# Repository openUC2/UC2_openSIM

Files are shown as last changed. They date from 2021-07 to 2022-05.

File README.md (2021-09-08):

<p align="left">

</p>

# openUC2 openSIM
---

This is the repository for the openSIM project which integrates structured illumination microscopy into the UC2-system.

🧾 The manuscript for the openISM and openSIM can be found under the [DOI:10.1101/2021.01.08.425840](https://doi.org/10.1101/2021.01.08.425840)

<p align="center">
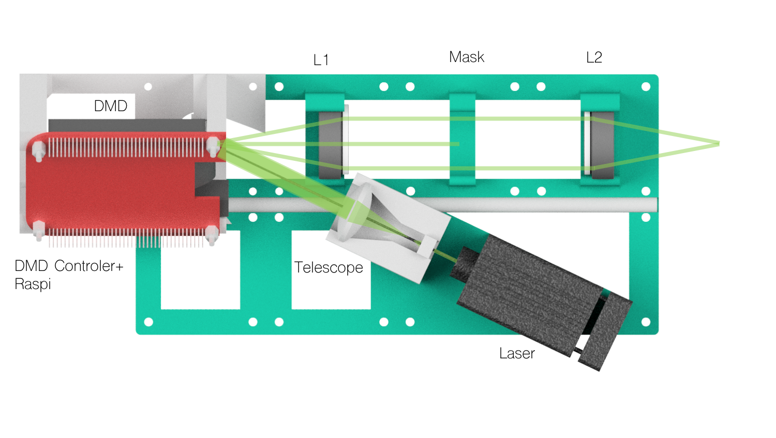
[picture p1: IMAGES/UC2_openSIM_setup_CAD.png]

</p>

***Fig 1:*** *This is the ready-to-print module which clicks into the UC2-system*

This module is based on the work by the Huser-Lab and can be found as a preprint on Bioarxiv [1]. It uses a low-cost single-mode diode laser (532 nm) and a Raspberry Pi driven DMD module to generate a structured illumination for microscopy. Since we use coherent illumination, we can create pattern suitable for SIM in order to increase the lateral resolution. So far we're not aiming for any super-resolution, but rather give a proof of principle.  

<p align="center">
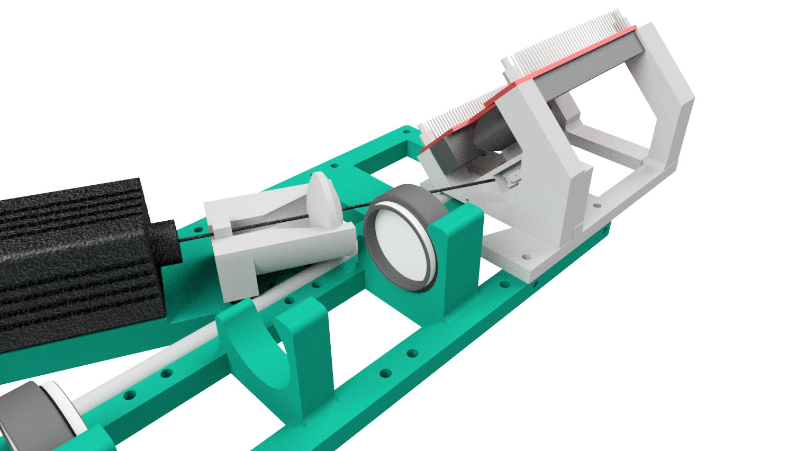
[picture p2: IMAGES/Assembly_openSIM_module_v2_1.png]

</p>

***Fig 2:*** *A beam-expander magnifies the collimated beam which hits the DMD displaying a set of gratings*

The angle between the collimated and expanded Laser-beam and the DMD is 25° in order to get the maximum in the diffracted orders.

[1] *DMD-based super-resolution structured illumination microscopy visualizes live cell dynamics at high speed and low cost
Alice Sandmeyer, Mario Lachetta, Hauke Sandmeyer, Wolfgang Hübner, Thomas Huser, Marcel Müller
bioRxiv 797670; doi: [https://doi.org/10.1101/797670](https://doi.org/10.1101/797670)*

***Features:***
- "True" two-beam SIM
- Very low cost:  ~400€
- Easy to align
- Open-Source
- One module per wavelength possible
- Various patterns possible

## Optical System

<p align="center">
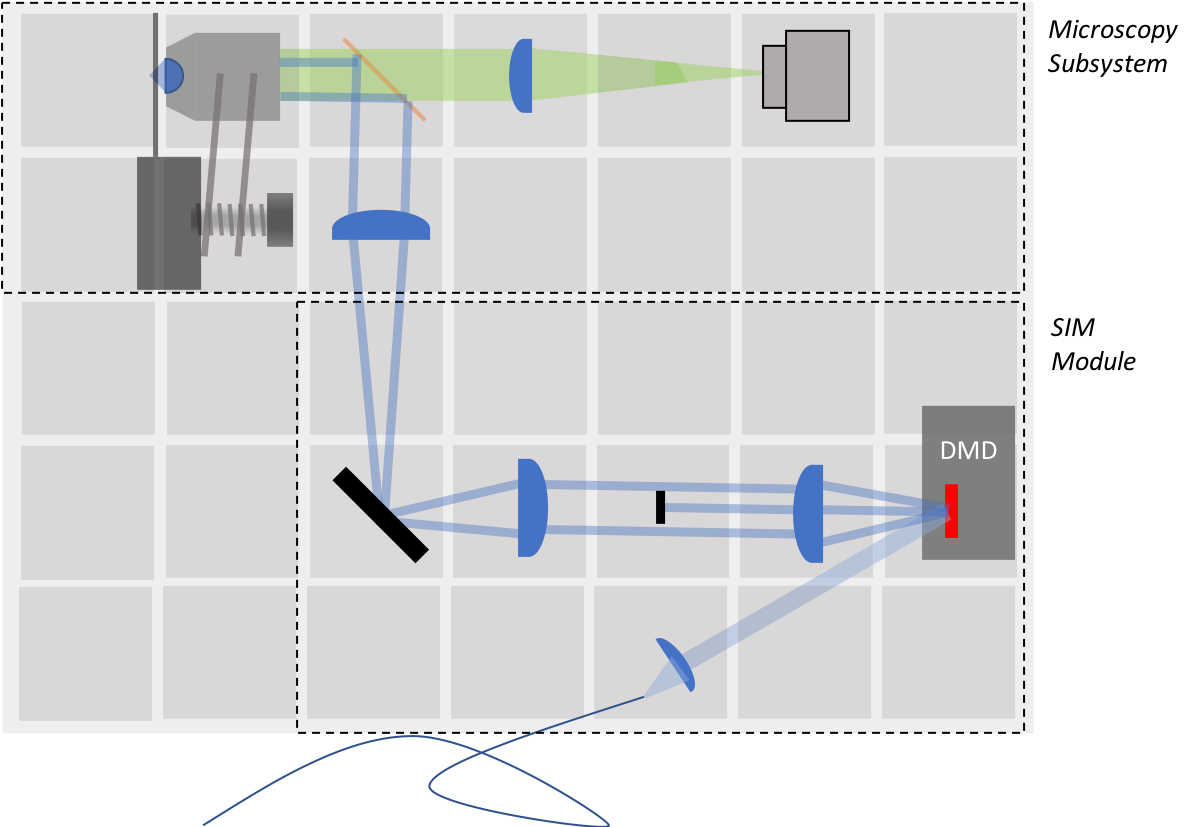
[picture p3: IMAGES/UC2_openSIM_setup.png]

</p>

***Fig 3:*** *The full system based on the modular cubes*

The system of a classical two-beam interference SIM is straight forward and based on common 4f (i.e. fourier imaging) system, where focal lengtheses of adjacent lenses are following each other. The core idea is to place two delta-peaks inside the BFP of the objective lens. The lens fourier-transforms the peaks and therefore form a grating in the sample plane.

In order to keep the whole system small, the telescope imaging the DMD is  based on two lenses with ***f'=50mm*** (e.g. Thorlabs achromates). A tube-lens of ***f'=180mm*** fourier-transforms the image folded by the mirror and places the different diffraction order inside the BFP of the objective lens. To produce 2D-Sim a fourier mask in the fourier-plane after the DMD, blocks the zeroth order.

The DMD, driven by a Raspberry Pi, gets illuminated by a more-less plane wave from a coherent laser source. The pattern which are displayed are then actually coherently reimaged inside the sample plane by the whole system.

# Table of Content
* **[Software](#-software)**
* **[Hardware](#-hardware)**
* **[Bill of materials](#-bill-of-materials)**
* **[Electronics](#-electronics)**
* **[Results](#-results)**

# Software
A dedicated Tutorial how to setup the software can be found in the [Readme_Software.md](Readme_Software.md).

# Hardware

Below we describe how the device can be build and assembled in order to replicate the whole system as shown in the rendering above [Align Tutorial](Readme_SIM_alignment_tutorial.md). One needs additional parts that can be found in the core [openUC2 repository](https://github.com/bionanoimaging/UC2-GIT).

## Bill of material

Below you will find all components necessary to build this device

### 3D printing files

All these files need to be printed. We used a Prusa i3 MK3 using PLA Prusament (Galaxy Black) at layer height 0.15 mm and infill 50%.

Parts to print:

* 1x [SIM-Module 2×4_Base](./CAD/30_CUBE_openSIM_base_v4.stl); [SIM-Module Lid](./CAD/30_CUBE_openSIM_Cagelid.stl)
* 1x [DMD holder](./CAD/30_CUBE_DMD_Holder.stl); [DMD Mount](./CAD/30_CUBE_DMD_Fixation_base.stl)
* 1x [Fourier Mask](./CAD/30_CUBE_Fouriermask.stl)
* 1x [Telescope for Beam Expansion](./CAD/30_CUBE_OpenSIM_Laser_Telescope_Mount.stl)
* 1x [Rod holder](./CAD/30_CUBE_openSIM_Rodholder.stl)
* 1x [Z-stage](https://github.com/bionanoimaging/UC2-GIT/blob/v3/CAD/ASSEMBLY_CUBE_Z-STAGE_sample/STL/20_Cube_Insert_Z-Focus_single_v3.stl)

### Additional parts
This is used in the current version of the setup

|  Type | Details  |  Price | Link  |
|---|---|---|---|
| Laser |  12V 638nm 300mw Fat Beam Laser Module |  40 € | [Laserland](https://www.laserlands.net/diode-laser-module/600nm-640nm-orange-red-laser-module/3258-638d.html)  |
| DMD |  Evaluierungsmodul (EVM) DLP® LightCrafter™ Display 2000 |  90 € | [Digikey](https://www.digikey.de/product-detail/de/texas-instruments/DLPDLCR2000EVM/296-47119-ND/7598640)  |
| Raspberry Pi | Raspi+SD-Card+Case+Powersupply(for DMD+Raspi, 5V, >=3A!) |  70 € | [Reichelt](https://www.reichelt.de/raspberry-pi-4-b-4x-1-5-ghz-1-gb-ram-wlan-bt-rasp-pi-4-b-1gb-p259874.html?PROVID=2788&gclid=Cj0KCQiAz53vBRCpARIsAPPsz8X9hCOt9yVVB_WqLCmKSs2e-KuThVnrMEtl2TRbAUTqtVoNZU3zM3YaAg2ZEALw_wcB&&r=1)  |
| Tube-lens | Lens, f=180mm |  10 € | [PGI-Versand](https://www.pgi-versand.de/?id=47&mode=artdet&artnr=564.OA.64)  |
| Telescope-lens | 2x Achromatic 1inch Lens, f=50mmmm |  82 € | [Thorlabs](https://www.thorlabs.com/thorproduct.cfm?partnumber=AC254-050-A)  |
| Dichroics  |  740IY 125 40x25mm|  35 € | [ComarOptics](https://www.comaroptics.com/components/filters/dichroic-filters/long-pass-dichroic-filters)  |
| Mirror | 1 inch Silver Mirror, Protected |  50 € | [Thorlabs](https://www.thorlabs.de/newgrouppage9.cfm?objectgroup_id=903)  |
| iPhone Lens | iPhone 5 lens for the telescope  (optional) |  5 € | [Amazon]()  |
| Lens | 25mm lens for the telescope (optional) |  5 € | [Amazon]()  |
| Cage rods  | 8 inch cage rod for 30mm cage system |  33 € | [Thorlabs](https://www.thorlabs.de/thorproduct.cfm?partnumber=ER8)  |
| PCB for Raspi-DMD connection  |  Various |  8 € | [See below]()  |
| Micrometre for z-stage  | Range 0 mm →25 mm |  30 € | [RS PRO](https://uk.rs-online.com/web/p/micrometers/7857878/)  |

### Design files
The original design files are in the [INVENTOR](./INVENTOR) folder. *FOR ANOTHER FORMAT, GET YOUR OWN FOLDER.*

### Electronics
A dedicated Tutorial which explains how to assemble and setup the electronics can be found in the [Readme_Electronics.md](Readme_Electronics.md).

### Optics

A dedicated Tutorial how to align the optical setup can be found in the [Readme_SIM_alignment_tutorial.md](Readme_SIM_alignment_tutorial.md).

## Showcase
This is just some stack where we measured the fluorescent signal on a Fluochart:

<p align="center">
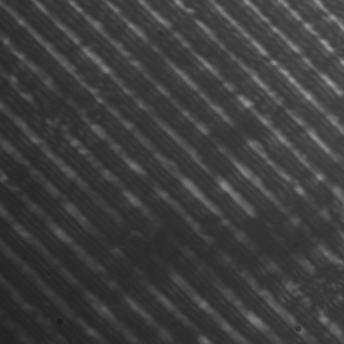
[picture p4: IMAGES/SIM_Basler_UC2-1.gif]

</p>

This is the result of the openSIM with a 100x 1.25 objective lens from China with Alexa Fluor 647 labelled microtubules. a) Widefield, b) SIM reconstruction on 2 angles and 5 phases

<p align="center">
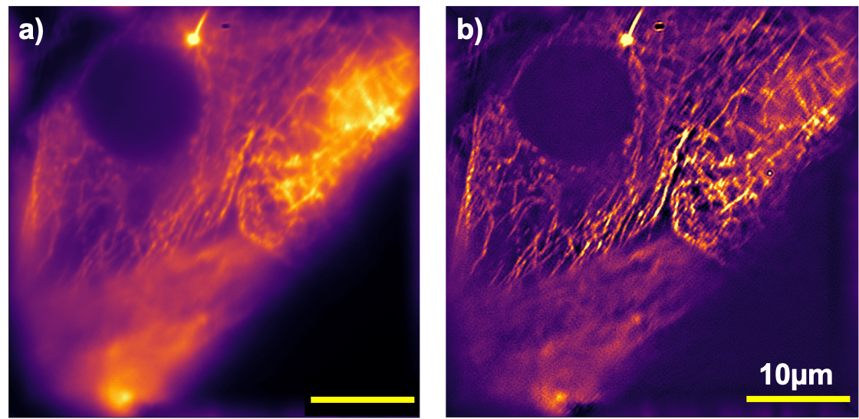
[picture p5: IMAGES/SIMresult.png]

</p>

## Get Involved

This project is open so that anyone can get involved. You don't even have to learn CAD designing or programming. Find ways you can contribute in  [CONTRIBUTING](https://github.com/openUC2/UC2-GIT/blob/master/CONTRIBUTING.md)

## License and Collaboration

This project is open-source and is released under the CERN open hardware license. Our aim is to make the kits commercially available.
We encourage everyone who is using our Toolbox to share their results and ideas, so that the Toolbox keeps improving. It should serve as a easy-to-use and easy-to-access general purpose building block solution for the area of STEAM education. All the design files are generally for free, but we would like to hear from you how is it going.

You're free to fork the project and enhance it. If you have any suggestions to improve it or add any additional functions make a pull-request or file an issue.

Please find the type of licenses [here](https://github.com/openUC2/UC2-GIT/blob/master/License.md)

REMARK: All files have been designed using Autodesk Inventor 2019 (EDUCATION)

## Collaborating
If you find this project useful, please like this repository, follow us on Twitter and cite the webpage! :-)

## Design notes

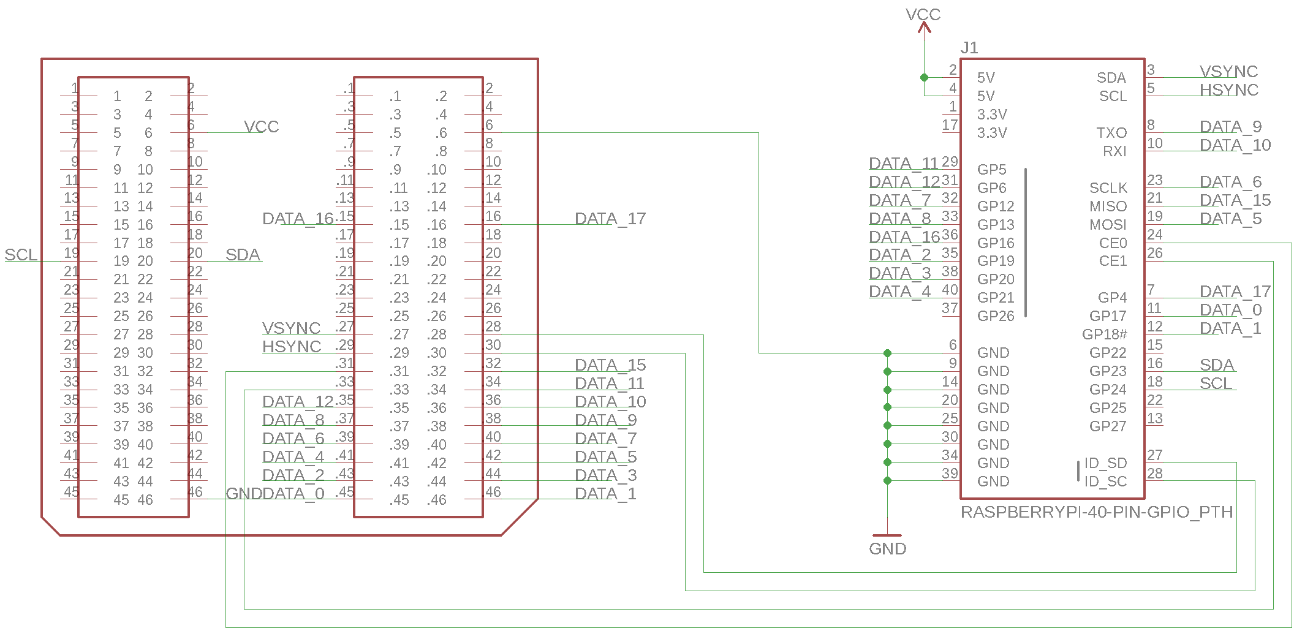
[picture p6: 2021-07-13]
ELECTRONICS/Piprojector/PiProjector.png

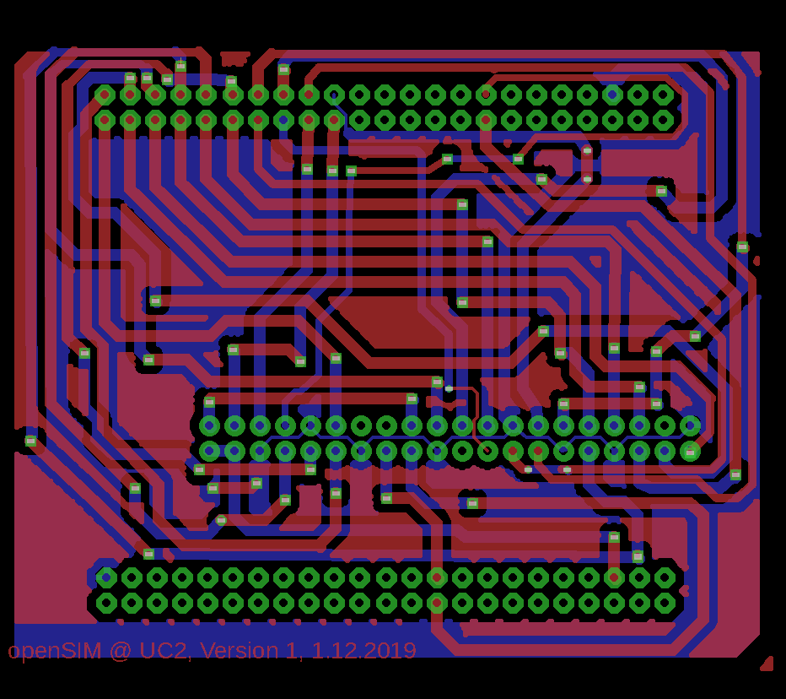
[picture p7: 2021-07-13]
ELECTRONICS/Piprojector/PiProjector_brd_all.png

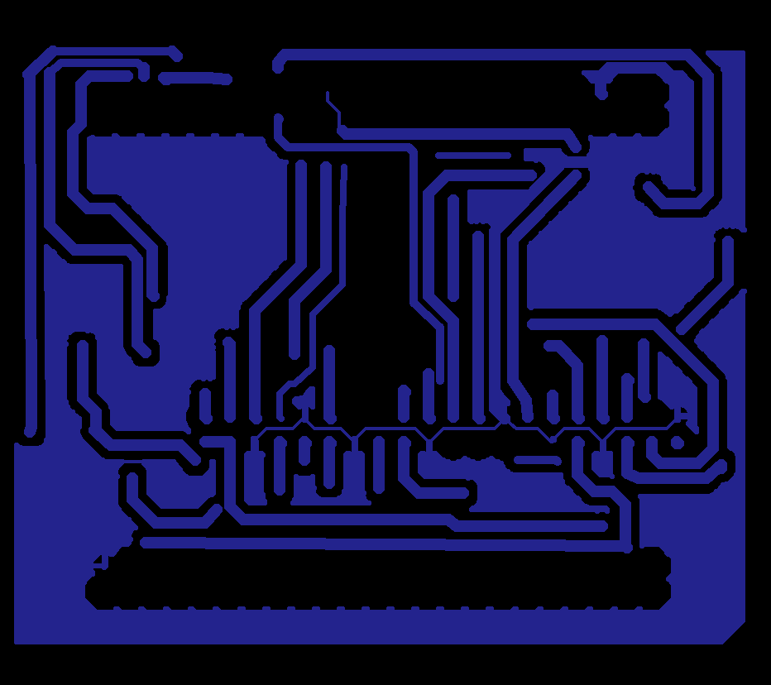
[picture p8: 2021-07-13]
ELECTRONICS/Piprojector/PiProjector_brd_bottom.png

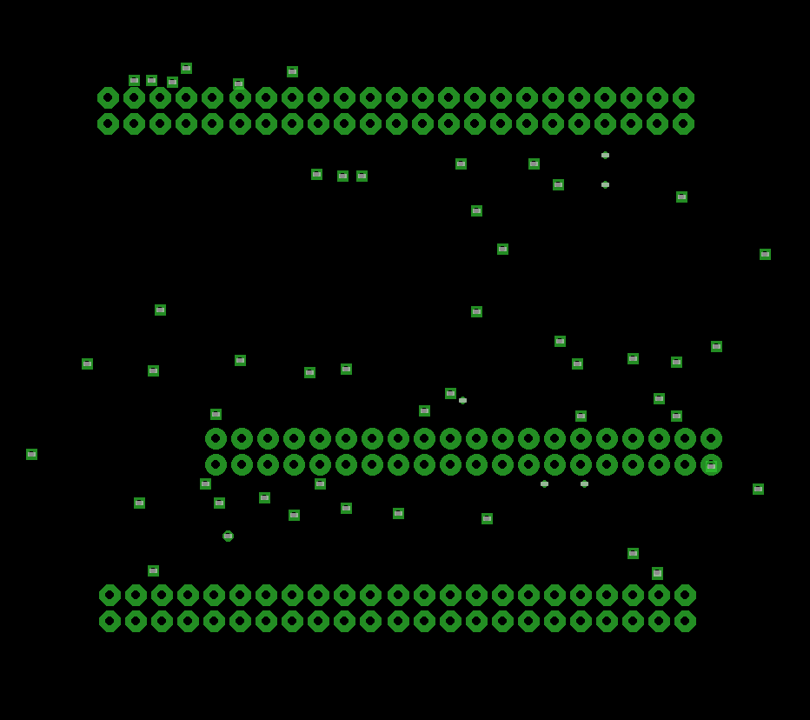
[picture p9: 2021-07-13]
ELECTRONICS/Piprojector/PiProjector_brd_pins_vias.png

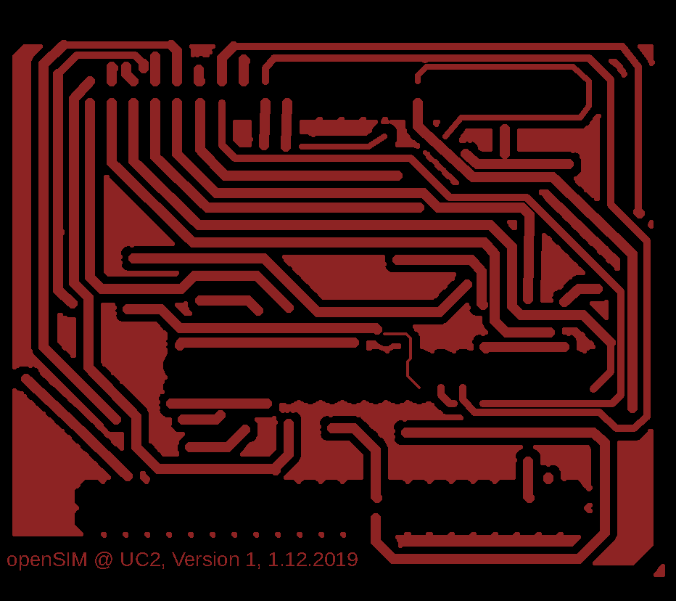
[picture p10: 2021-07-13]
ELECTRONICS/Piprojector/PiProjector_brd_top.png

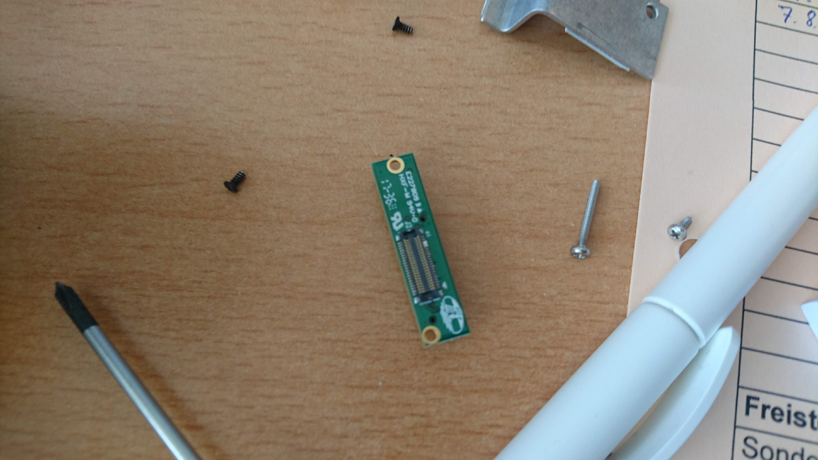
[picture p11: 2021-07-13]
IMAGES/UC2_DMD_4.jpg

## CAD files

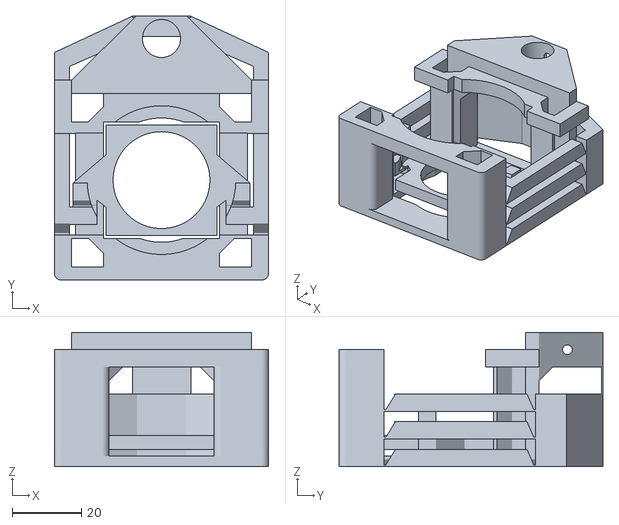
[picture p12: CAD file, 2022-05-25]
CAD/20_Cube_Insert_Z-Focus_single_v3.stl
62.0 x 76.4 x 38.8

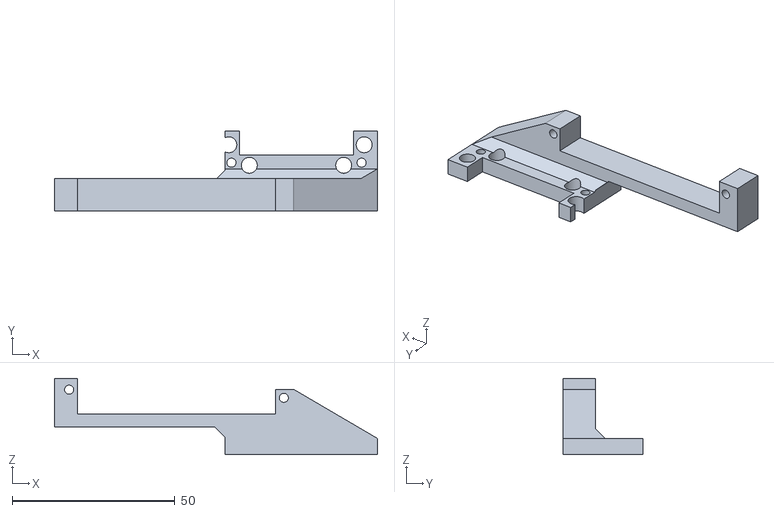
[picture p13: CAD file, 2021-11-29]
CAD/30_CUBE_openSIM_DMD_Raspi_holder.stl
99.3 x 24.7 x 23.5

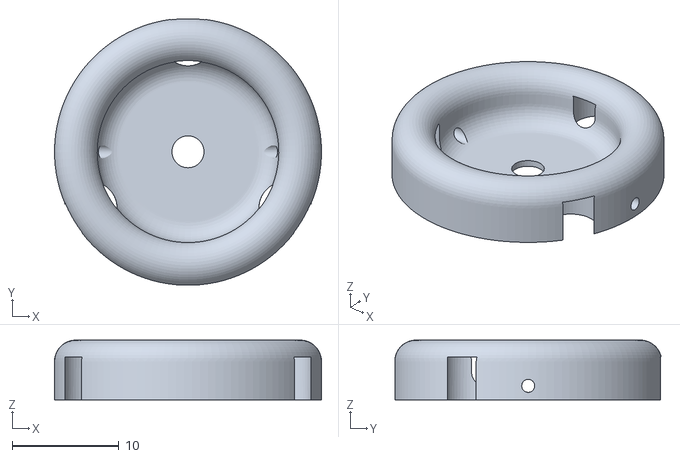
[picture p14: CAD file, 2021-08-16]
CAD/30_CUBE_openSIM_Fouriermask.stl
25.0 x 24.9 x 5.59

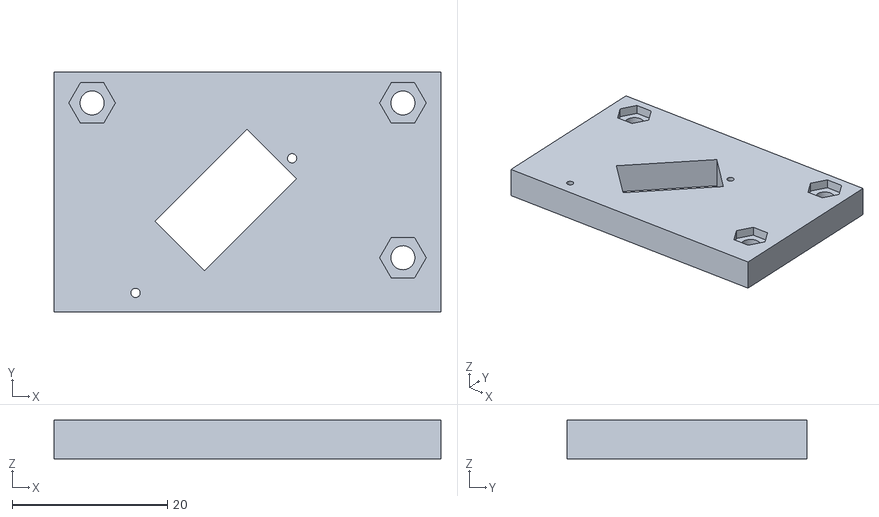
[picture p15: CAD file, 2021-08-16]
CAD/30_CUBE_openSIM_DMD_Holder.stl
49.8 x 30.9 x 5.00

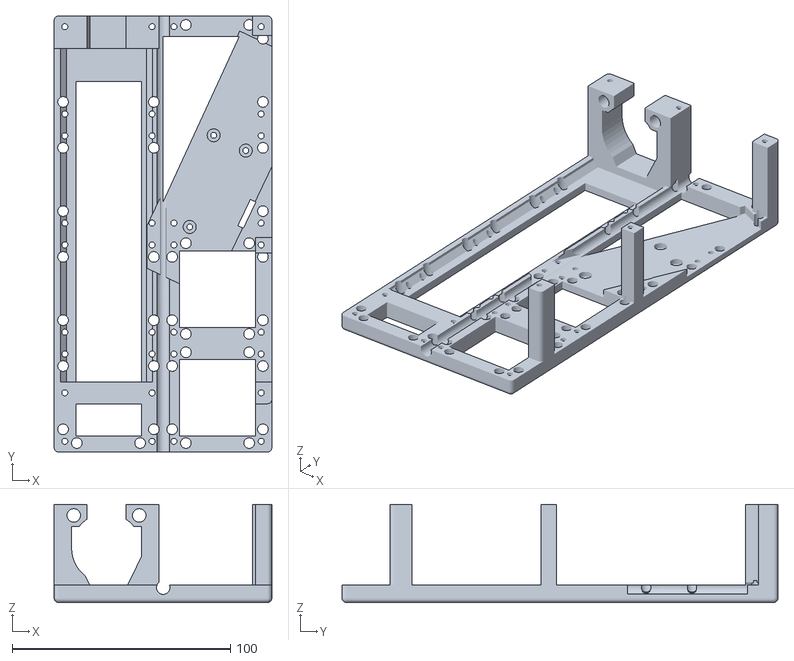
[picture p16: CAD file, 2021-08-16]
CAD/30_CUBE_openSIM_base_v4.stl
99.8 x 199.8 x 44.9

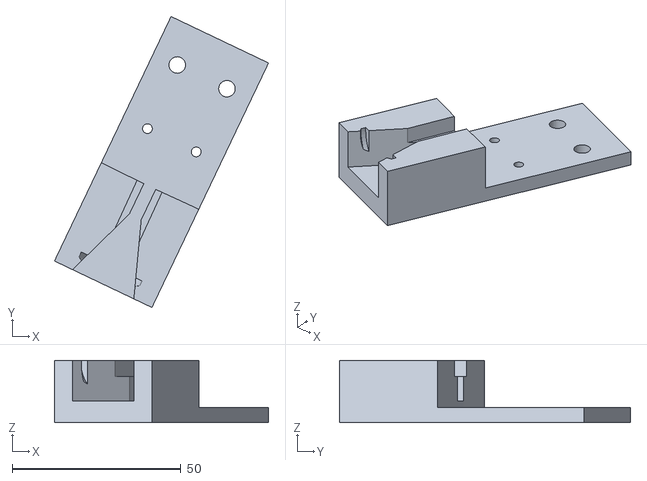
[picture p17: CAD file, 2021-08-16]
CAD/30_CUBE_openSIM_Laser_Telescope_Mount.stl
63.4 x 86.2 x 18.5

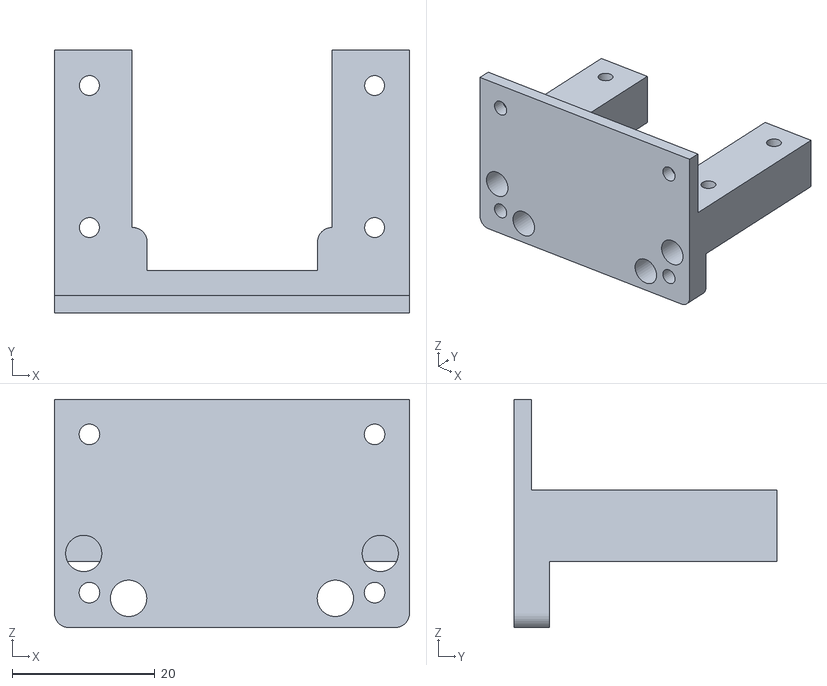
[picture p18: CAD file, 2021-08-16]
CAD/30_CUBE_openSIM_DMD_Fixation_base.stl
49.8 x 36.9 x 32.0

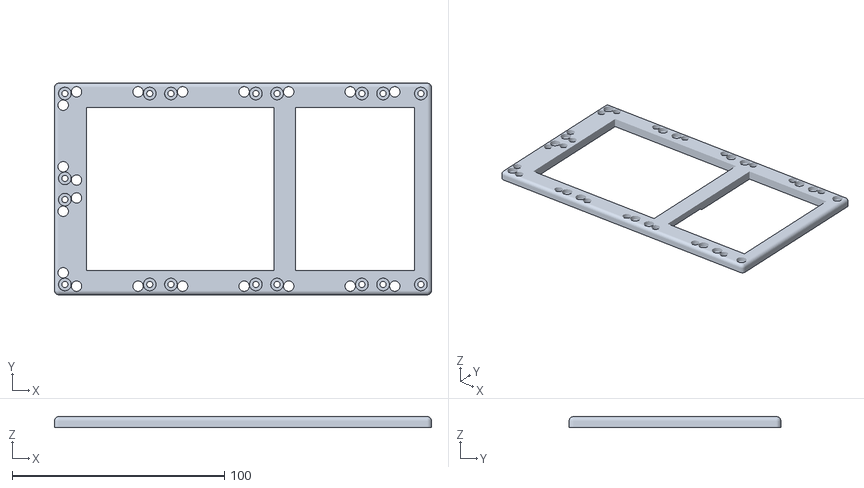
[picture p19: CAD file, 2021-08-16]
CAD/30_CUBE_openSIM_Cagelid.stl
177.7 x 99.8 x 5.08

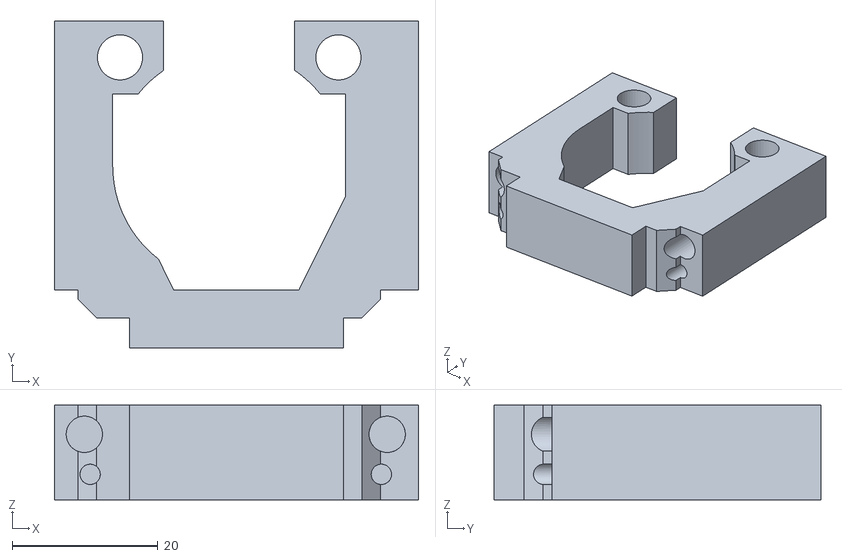
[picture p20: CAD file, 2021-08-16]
CAD/30_CUBE_openSIM_Rodholder.stl
50.0 x 44.9 x 13.0

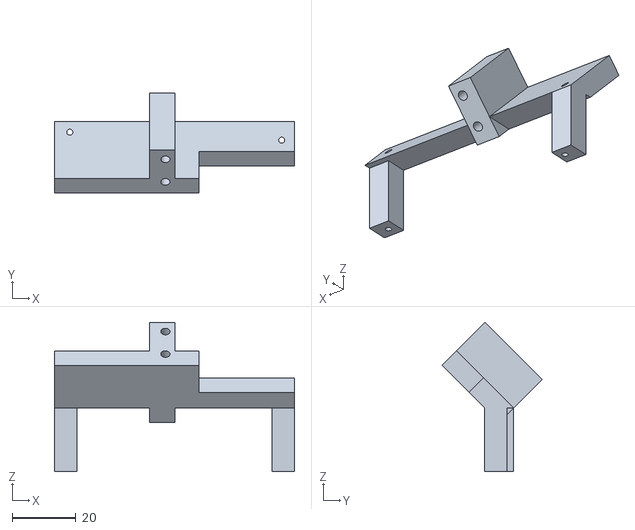
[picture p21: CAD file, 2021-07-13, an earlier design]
OLD/ASSEMBLY_CUBE_openSIM/30_CUBE_openSIM_DLP200EVM_Holder.stl
75.3 x 31.4 x 46.9

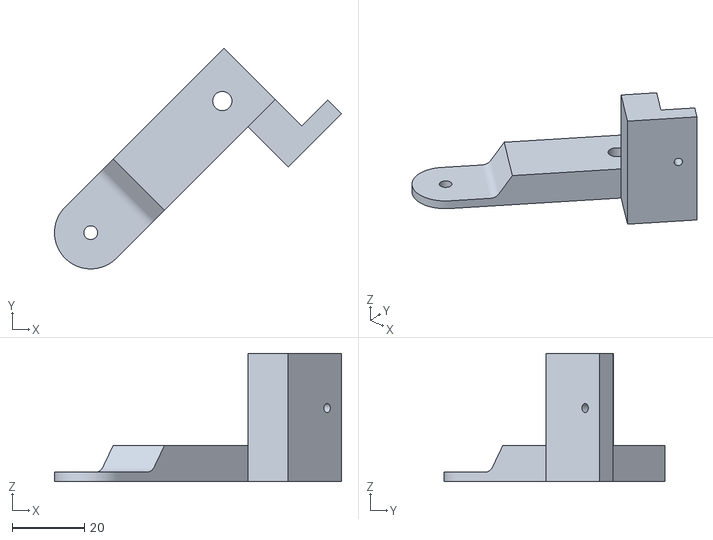
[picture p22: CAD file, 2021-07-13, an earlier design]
OLD/ASSEMBLY_CUBE_openSIM/30_OpenSIM_Arm.stl
79.2 x 60.9 x 35.4

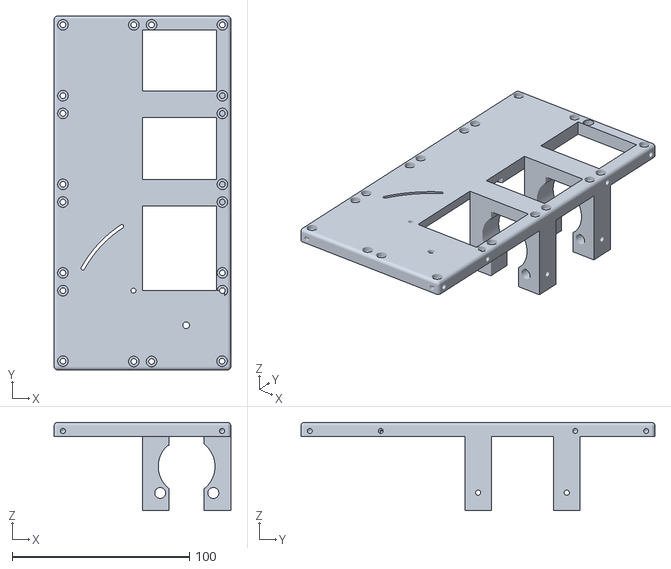
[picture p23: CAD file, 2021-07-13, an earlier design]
OLD/ASSEMBLY_CUBE_openSIM/30_CUBE_openSIM_base.stl
99.8 x 199.8 x 49.9

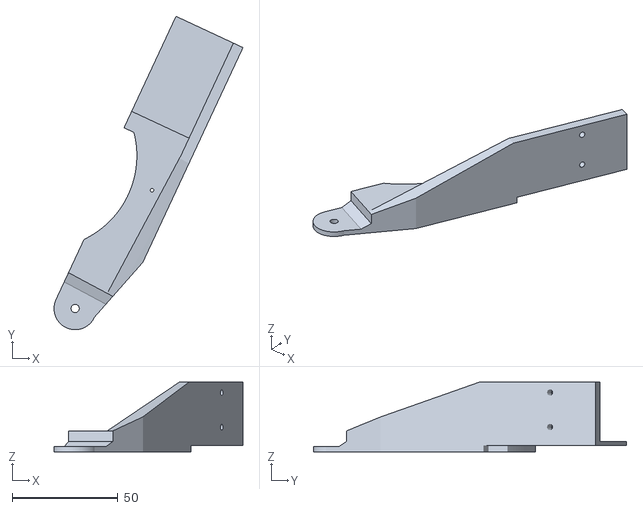
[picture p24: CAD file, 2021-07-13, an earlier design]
OLD/ASSEMBLY_CUBE_openSIM/30_CUBE_openSIM_Laserarm_532nm.stl
89.2 x 147.9 x 33.0

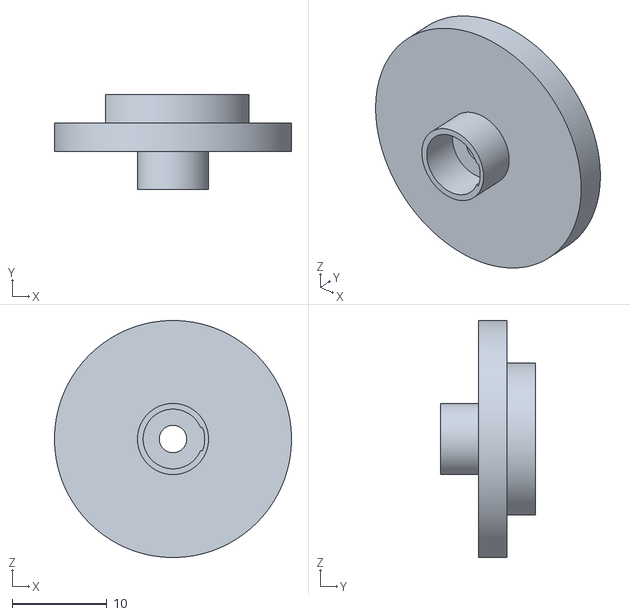
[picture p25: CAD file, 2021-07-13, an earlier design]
OLD/ASSEMBLY_CUBE_openSIM/30_Laser_FPC_Mount_collimator.stl
25.0 x 10.00 x 25.0

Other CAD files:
OLD/ASSEMBLY_CUBE_openSIM/30_CUBE_openSIM_DLP2000_Holder.stl

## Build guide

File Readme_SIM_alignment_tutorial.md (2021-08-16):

# SIM alignment tutorial

This tutorial is aming to align the openSIM module of the UC2 modular 3D printed microscope. The fundamental is a set of full prepared components in hand, which listed in the [here](README.md) for openSIM. The parts used for aligning the system are:

  - openSIM module
  - optical components
  - UC2 cubes and inserts
  - target sample
  - magical hands
## openSIM module
The illumination part for openSIM is a separate assembled module in a 3D printed cage with dimension of 2x4 UC2 cubes. In order to compatible with other UC2 cubes, the cage need to have M5 set screws at connection position. The DMD chip should be disassembled and mount onto the [DMD holder](./CAD/30_CUBE_openSIM_DMD_Holder.stl) with its own screws. The holder is connect to the base part with m3 screw and in between have springs. The configuration allows us to slightly adjust the direction of DMD. The whole part looks like that:

<p align="center">

</p>

***Fig. 1*** *An example image of the mounted DMD chip into the openSIM module.*

All the optical components should insert into Thorlabs cage system and fix with the rods like here:

<p align="center">

</p>

***Fig. 2*** *Optical path installation in the openSIM module*

## Align the camera
In the openSIM setup, the camera module is arranged on the bottom layer, therefore, it needs to focus to infinity first. Try to find a far away object (e.g a building or mountain) and image it with the camera clearly by adjusting the distance between the camera and the tube lens. Following image shows an example image took by an infinity-focused camera.

<p align="center">
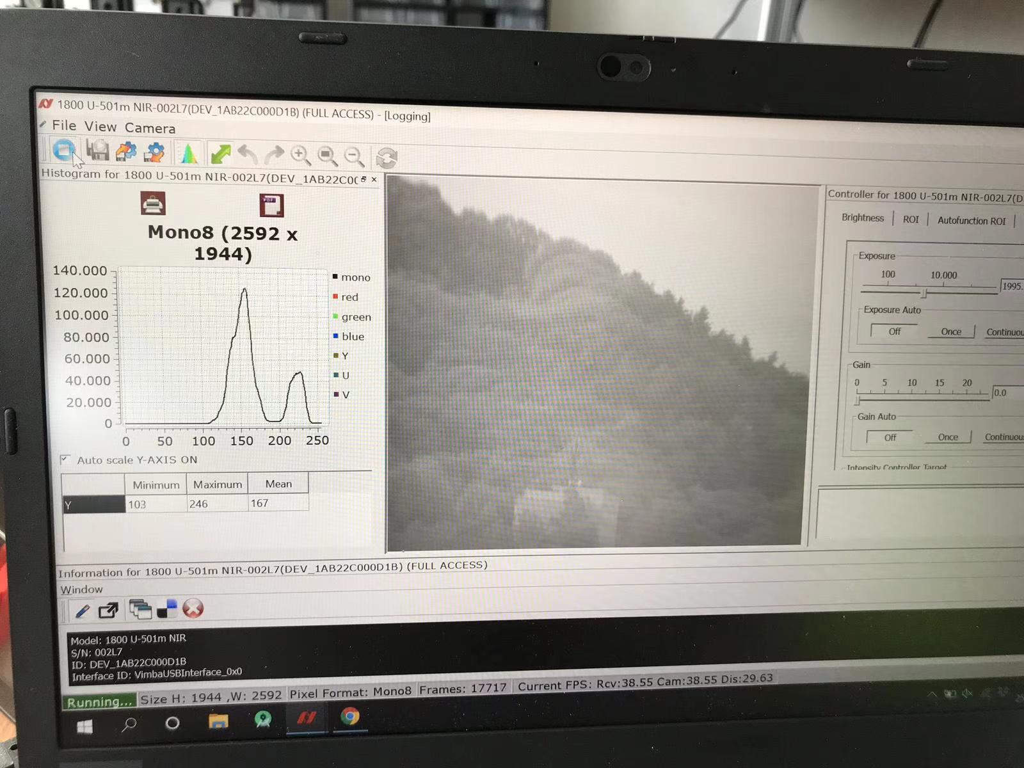
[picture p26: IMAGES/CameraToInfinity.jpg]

</p>

***Fig. 3*** *An example image of an infinity-corrected camera. The mountain on the picture is far away from our office.*

When the camera is infinity-focused, the bottom layer of the system can be placed as shown here:

<p align="center">
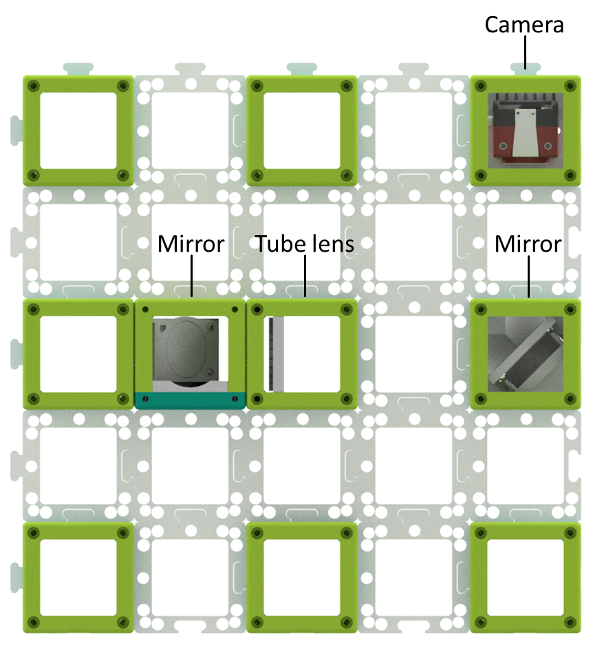
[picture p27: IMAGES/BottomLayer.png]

</p>

***Fig. 4*** *A top view of the system's bottom layer which contains camera module. This layer consists of camera and some empty cubes as support.*
	
In this layer, it has some empty cubes spread around in order to support the upper layers.

## Align the illumination laser source
The laser we used is a 638 nm diode laser. In order to get a bigger spot size to illuminate the active area of the DMD, the collimation lens in front of the laser is removed and a 20 mm lens collimating the convergent beam again is set in front of this assembly. Move the laser on its mount back and forth to collimate the laser. Check the beam size in front of the lens as well as far away, it should keep the same size and larger than the mirror array of the DMD. For more information, please also have a look in this [tutorial](../CAD/ASSEMBLY_CUBE_Beamexpander_v2).

<p align="center">
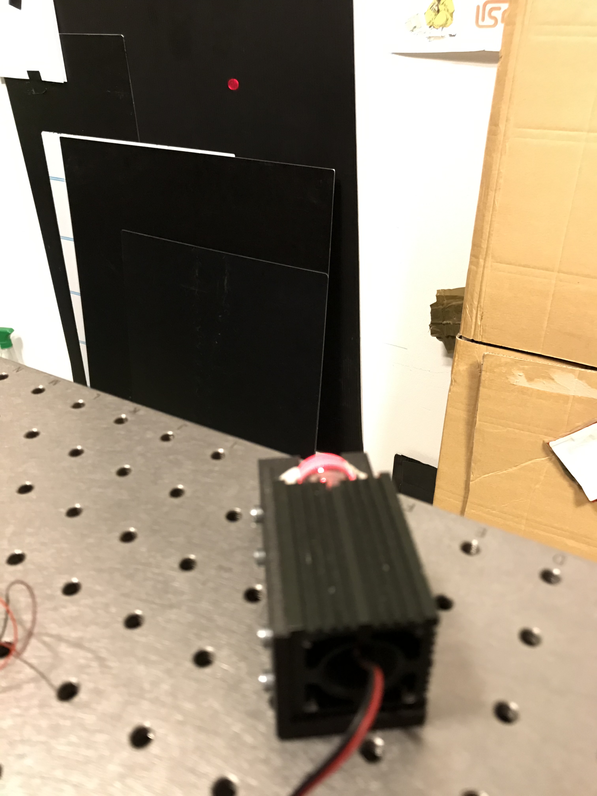
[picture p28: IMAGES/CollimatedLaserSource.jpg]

</p>

***Fig. 5*** *The laser beam is collimated by the 20 mm lens and the beam size doesn't change with the propagation distance.*

## Prepare Fourier mask 

The telescope consists of two 50mm achromatic lenses and a fourier mask, which block the zero-order illumination and regenerate the intermediate image of the DMD at the focus the second lens. The telescope is fixed in the openSIM module.

<p align="center">
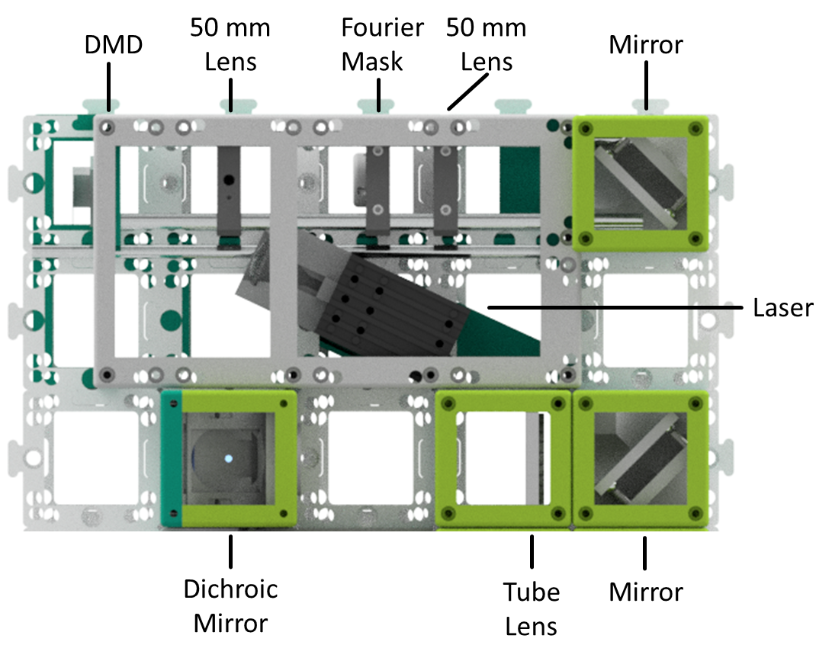
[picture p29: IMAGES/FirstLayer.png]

</p>

***Fig. 6*** *Illumination part of the openSIM setup. The laser beam is expanded and illuminates on the DMD mirror area. The zero-order of the beam is blocked in the first telescope, the two first-order beam will focus and interference at the sample plane with the tube lens and objective.*

A 3D printed Fourier mask is applied in the telescope, the 3D model of the mask case can be found in the ``STL`` repository. One thin copper wire is splitted from electric cable, first make a small knot on the wire which is roughly the size of the desired tin drop. Then solder a small drop of soldering tin onto the knot.

<p align="center">
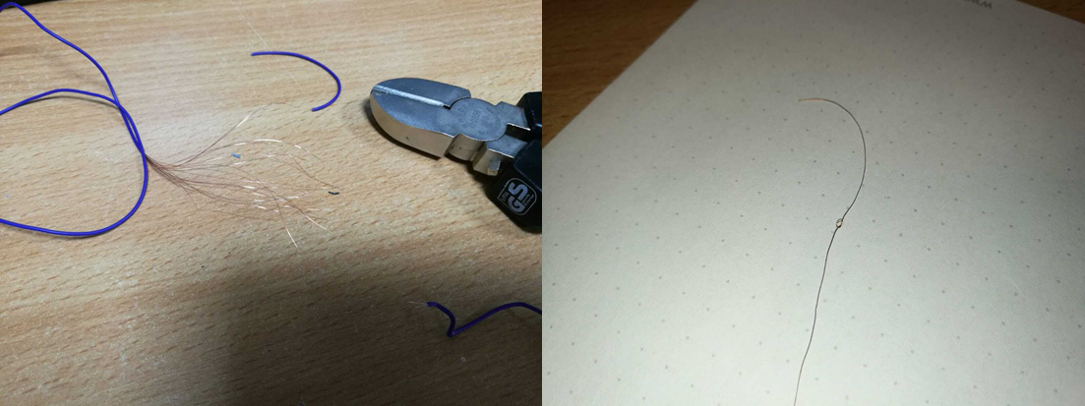
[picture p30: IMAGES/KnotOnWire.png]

</p>

***Fig. 7*** *A single copper wire is taken from an electrical cable (left), a knot is crossed on the wire and can easliy add correct size of soldering tin on it.*

Mount the wire on the 3D printed part with the help of glue or fix gum, such as [UHU Patafix](https://www.uhu.de/de/produkt.3311). In order to aviod unexpected reflextion of the soldering tin, we can use black color marker pen and paint on the tin drop. At the end, the tin drop should be positioned at the middle of the mask. 
 
<p align="center">
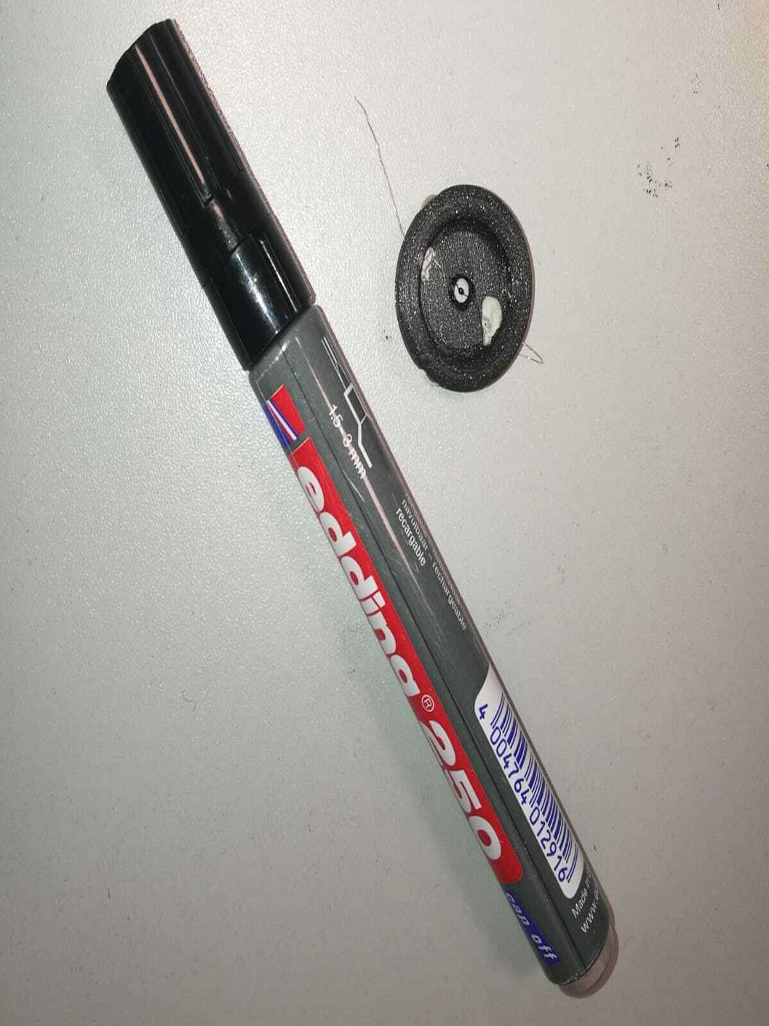
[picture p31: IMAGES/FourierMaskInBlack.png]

</p>

***Fig. 8*** *A prepared Fourier mask which has a soldering tin painted with black on it. The copper wire is fixed with fix gum.*

## Alignement of the first Achromat

First we want to make sure, that the achromate lens which faces the DMD does a proper Fourier transform by means of placing it exactly one focal length away from the DMD. 
It is of great help to start with a collimated light source such as a Laser diode/pointer (or any other collimated light source) inside an [UC2 laser cube](../CAD/ASSEMBLY_CUBE_Beamexpander_v2) which will produce the focal spot within the focal lenght of the lens. The laser is placed directly in front of the exit of the openSIM module i.e. the position of the first reflecting mirror out of the SIM module. This has to coincide with the DMD mirror plane. In order to make the two planes matching, you have to move the achromatic lens back and forth. You will find the proper position, when the diffraction pattern of the DMD (reflection) has the smallest spots. 

## Alignment of the telescope

The goal is to have a plane wave in- and outcoming of the telescope consisting of the two 50mm achromates. Now, we have to insert the second achromatic lens. We use the collimated light source to  and heading to the DMD mirror, if the telescope is good calibrated, the laser beam should illuminate onto the DMD chip with its original spot size. After all alignment the lid of the openSIM moudle should be mount with M4 screws.

## Bring the system to the table

### Setup the Raspberry Pi
The DMD is controlled by Raspberry Pi, when the Raspberry Pi connected with the DMD we need to remote control it with a PC for display images. For transport the generated illunimation images or python code to raspberry pi, using [WinSCP](https://winscp.net/eng/download.php) on Windows or [Putty](https://www.putty.org/) on Mac makes it easier.

Turn on a WiFi Hotspot such as
```
SSID: Blynk
Password: 12345678
```
Turn on the Raspberry Pi and wait until it connects. Note the IP Address of the Pi (in our case ```192.168.43.9```). Connect to the Pi with SSH on you computer using the following line:
```
ssh pi@192.168.43.9
```
The default password of Raspberry Pi is ``raspberry``. Then we need to activate the external display of Raspi with the command:
```
export DISPLAY=:0
```
The grating pattern we used is generated by a python script ``pygame_grating.py``. The grating is default set in vertical direction and the grating constant is 6 pixel size of the DMD micromirror and rolling 1 pixel distance in each second. You can end the infinite loop with ``Ctrl + C``.

### Coarse adjustment of the mirrors
The setup has two mirrors to direct the illumination beam to the objective. The aim of adjust the mirrors is to reflect the laser beam straightly into the objective. The mirror has three directional flexibilities which can be changed by the screws behind the kinetic mirror mount. The mirrors should be plugged onto the base one by one, and after each mirror the propagation direction of the beam should stay the same with the optical axis.

When raw adjustment is done, set the tube lens and the dichroic mirror at their position, the frequency of the DMD image should be located and focused at the position of the back focal plane of the objective. When the python script ``pygame_grating.py`` is running on the Raspberry Pi, three beams should located at the center of the cube.
For proper alignment make sure the following steps are met:
- zero order is going through the center of each cube (i.e. optical axis)
- +/-1st diffraciton order is symmetrically oriented inside the BFP (e.g. place a paper in the position of the BFP and tune the mirrors 1/2)

<p align="center">
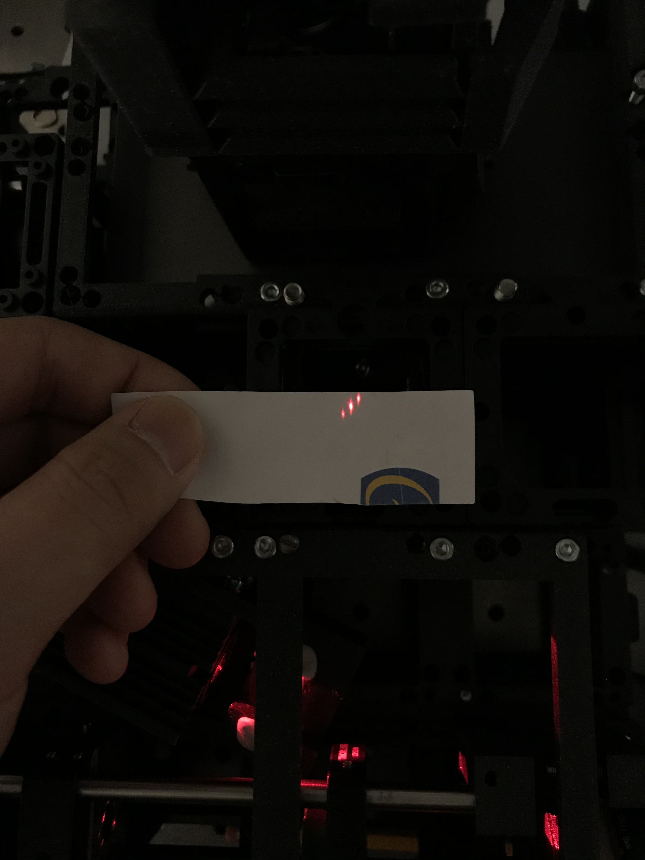
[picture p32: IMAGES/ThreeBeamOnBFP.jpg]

</p>

***Fig. 9*** *Three beam pattern should locate at the center of the back focal plane of the objective.*

### Fine adjustment of the mirrors

Insert the [objective cube and linear z-stage](../CAD/ASSEMBLY_CUBE_Z-STAGE_v3) with bright LED illumination (***PLEASE UPLOAD ME***) above the dichroic mirror, use one surface reflecting sample, such as a [negative Thorlabs USAF Target](https://www.thorlabs.com/thorproduct.cfm?partnumber=R3L1S4N). Move some structures of the target into the field of view, and adjust the linear stage to focus on the structures sharply. At that time, it should be some unclear DMD illumination signal on the sample. (When not, it is recommanded to go back to adjust the direction of the two mirrors, make the propagation direction of the laser beam parallel to the axial direction of the objective.) Keep the target structure sharp and adjust the two mirrors, make the illumination pattern sharp at the sample plane. With a three beam interference, the image generated by ``pygame_grating.py`` with grating constant of 6 pixel size should look like this:

<p align="center">
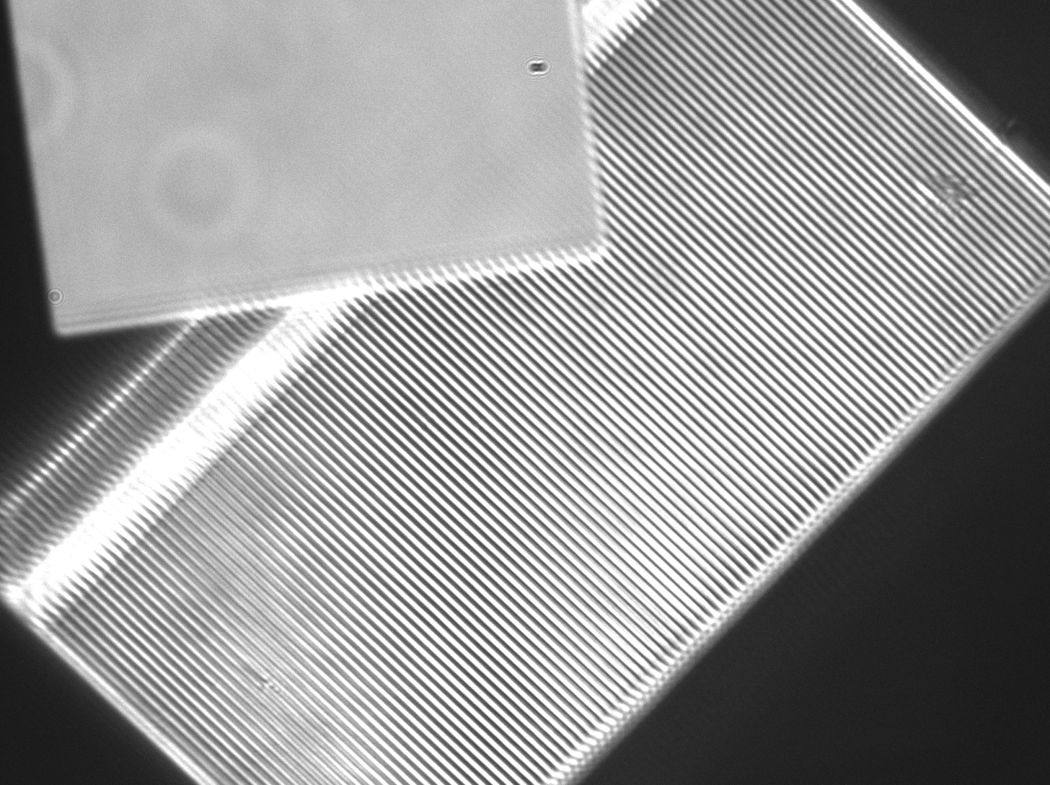
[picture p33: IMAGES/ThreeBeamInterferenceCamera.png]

</p>

***Fig. 10*** *Three beam interference at the sample plane. Left above is a structure from the USAF target, right grating is the illumination pattern from the DMD.*

***Troubleshooting***: 

- *Sample and illumination plane do not coincide:* Try to carefully move the 50mm achromatic lens (L2) 
- *I see a black bar blocking my sample on the camera:* Try to adjust the mirror facing the camera to move the picture that the center of the optical axis coincides with the camera chip.

## Adjustment of the Fourier-filter

Then remove the objective from the system and place a piece paper in the position of the BFP. Now insert the Fourier filter on the metal plate inside the openSIM module. Try adjusting the position of the Fourier mask in XY in the telescope to block such that the tin drop blocks the zero-order of the illumination. Make sure you block the zeroth "harmonic" of the diffracted light from the DMD (i.e. highest intensity in the Fourier plane). Make sure, that the thin wires won't block or disturb the first order signal (e.g. rotate it slightly). To check the process, hold a small piece of paper at the position of the back focal plan, their should be only two first-order spot left like this:

<p align="center">
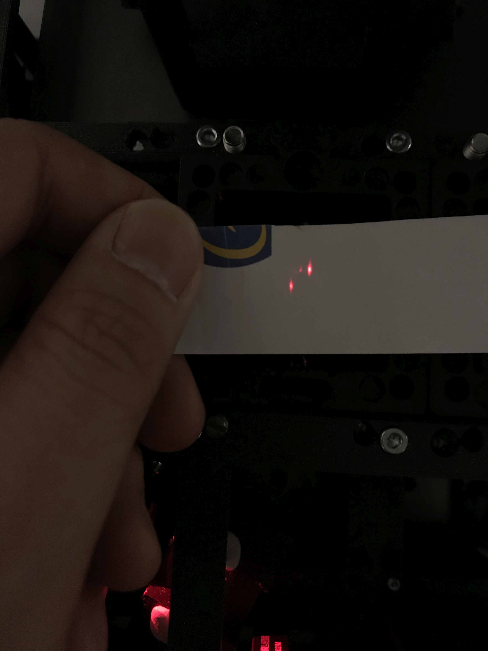
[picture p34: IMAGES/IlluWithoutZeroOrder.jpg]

</p>

***Fig. 11*** *Using the Fourier mask to block the zero-order illumination. You can easily check the block efficiency with a paper by removing the objective from the system.*

Place the objective back, put again a paper slightly above the sample plane, you should observe two same-shaped beam spot. 

<p align="center">
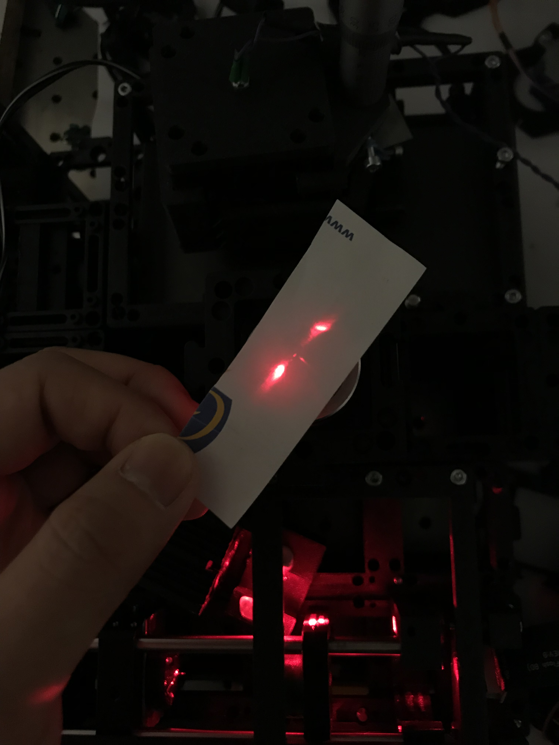
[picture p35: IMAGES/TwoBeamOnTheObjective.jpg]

</p>

***Fig. 12*** *The two beam is interferencing at the sample plane and divergent above the sample plane.*

Refocus onto the target sample, the two beam interference pattern should be shown on the camera. If not, try to slightly tilt the mirror to refocus the both patterns on the sample plane. A example image is shown as below:

<p align="center">
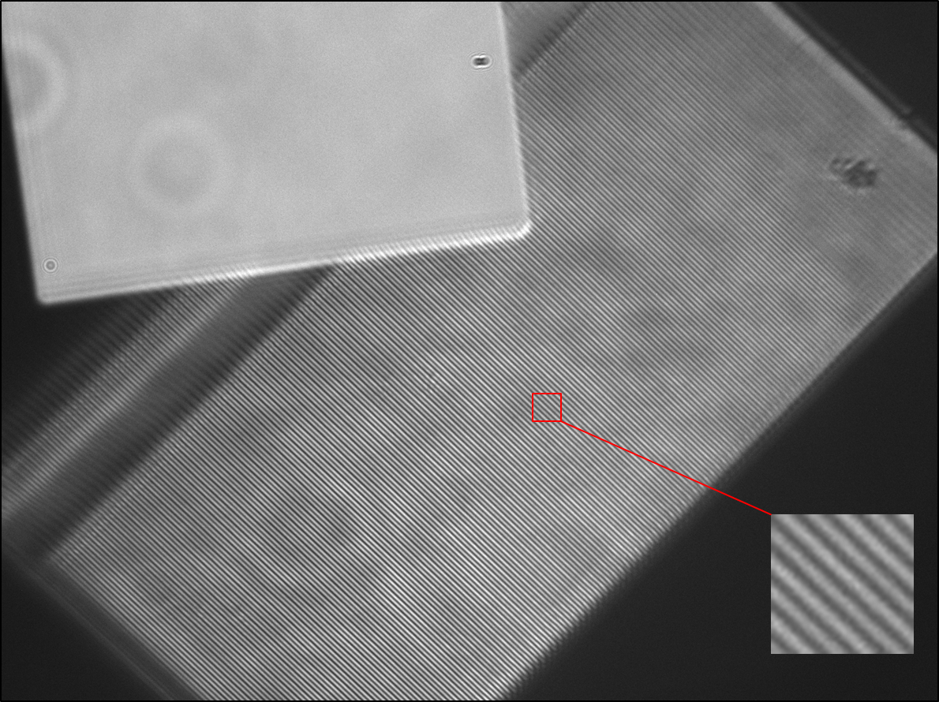
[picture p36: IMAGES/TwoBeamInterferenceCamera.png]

</p>

***Fig. 13*** *The expected two beam interference pattern on the camera. Right side is the detail of the interference pattern.*

## Ready for play

Now the openSIM setup is ready to play. Enjoy the new toy!

<p align="center">
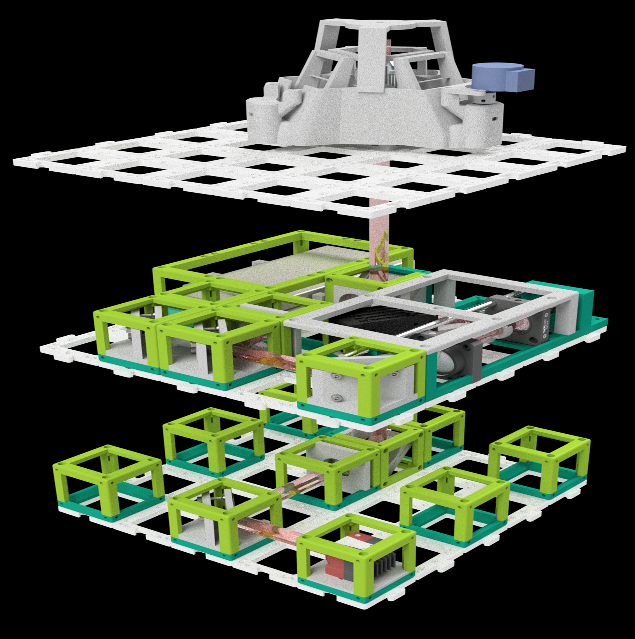
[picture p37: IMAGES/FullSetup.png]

</p>

***Fig. 14*** *Overview of the SIM/ISM setup.*

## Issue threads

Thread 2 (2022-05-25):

### ISSUE TITLE
More BoM details

### ISSUE THREAD

**Issue by rwb27** [openUC2/UC2_openSIM#2]
Hello,
  I'm hoping to build one of these with a masters student this semester and am ordering the parts.  From the BoM on the readme page, I have currently ordered/obtained:

From Farnell/OneCall:
*  DMD |  Evaluierungsmodul (EVM) DLP® LightCrafter™ Display 2000 
* Raspberry Pi and accessories

I will order/have:

From ThorLabs:
* 2x Achromatic 1inch Lens, f=50mmmm
* 4x 8 inch cage rod for 30mm system
* 1" silver mirror
From RS:
* Micrometre for z-stage 

**Questions**:
* Tube-lens (Lens, f=180mm,  10 €, [PGI-Versand](https://www.pgi-versand.de/?id=47&mode=artdet&artnr=564.OA.64) ) what is the diameter, and is it an achromat?
* Dichroics: what size is needed, and is it just the standard excitation/emission/45 degree set for whatever fluorophore we're using
* iPhone lens: do you know what focal length I'm looking for, roughly?
* 25mm lens for telescope: is this an achromat, and what diameter does it need to be? 
* Related question: what's the target beam size on the DMD? I guess that sets the ratio of lenses in the telescope?

**Comment by beniroquai** [comment]
Hey Richard, 

thanks for reaching out! There have definitely been some updates here and there. The [assembly-guide](https://github.com/openUC2/UC2_openSIM/blob/main/Readme_SIM_alignment_tutorial.md) seems to be a bit more up to date. @ranranking, would you mind having a look at the [README](https://github.com/openUC2/UC2_openSIM/blob/main/REAMDE.md) and check if this is still ok? The renderings seem to be a bit old. 

The most important things you would need to get in order to get some SIM pattern in your sample plane are:

*Talking only about the openSIM module:*
[!](https://github.com/openUC2/UC2_openSIM/raw/main/IMAGES/OpticalPath.jpg)

* a laser, which wavelength? (532nm usually has great mode profile, 635nm usually works nice with a large variety of bright fluorophores => good for raspi cam); Beam-Diamter ~4mm 
* the proector (that's the DMD you mentioned)
* a 4f' system created by the 2 50mm achromats 
* the Fourier mask (wire + lead drop) + 3 magnets and ferromagentic plate 
* the rods for stabilization + thorlabs cage plates 
* 2 thorlabs cage plates for the 4f system + Fouriermask
* the magnets and screws for the UC2 system 
* some M3 cylindrical head screws
* a set of 4 springs for aligning the DMD
* some lenses (including the iphone lens) to form the beam expander (secondary lens has to be chosen - beam expander module has to be updated accordingly; We widened the beam quite a lot to have less fast-axis problems
* 


I think we need to put that into the new Readme.



**Q/A:**

`Tube-lens (Lens, f=180mm, 10 €, PGI-Versand ) what is the diameter, and is it an achromat?`
That'S a glassblock of 50mm diameter; It'S cheap and works well :-) 

`Dichroics: what size is needed, and is it just the standard excitation/emission/45 degree set for whatever fluorophore we're using`
Filters: 25mm, Dichroic 26*34 (@ranranking ?) - I think Comar does not sell the IY740 anymore.. are you aware of any alternative sources @rwb27 ? 

`iPhone lens: do you know what focal length I'm looking for, roughly?`
I think the iphone 4/5 has f'=4.2mm and NA=.21

`25mm lens for telescope: is this an achromat, and what diameter does it need to be?`
I remember that we had to change this due to space limitations. Alternative was: Remove the colimating lens of the laser and place the lens (not achromat though) at the focal lenght's distance away from the diode to illuminate the DMD. 

`Related question: what's the target beam size on the DMD? I guess that sets the ratio of lenses in the telescope?`
~20mm to fully overshine the aperture and have a ~homogenous illumination.. The red laser was quite light-sheet-ish ;-)

**Comment by beniroquai** [comment]
One more add regarding the cellphone lenses. Most likely you know [this paper](https://journals.plos.org/plosone/article?id=10.1371/journal.pone.0095330) already?

**Comment by rwb27** [comment]
Great, thanks.  I hadn't seen that paper but it does a nice job on resolution, field of view, and field flatness - I like it!

I think I'll prioritise ease over cheapness and use a ThorLabs LA1399 for the tube lens, hopefully it's close enough.  

I'll check what dichroics I have, and probably order some from comar or thorlabs in due course.  I don't know any easy alternatives to Comar or ThorLabs, would love to find them!

I'm not sure you actually specified the **diameter of the 25mm lens** - I'll assume probably it has to be quite big, like 25mm diameter, if we're expanding the beam to fill the DMD, though perhaps that bit is (a) easy to change and (b) depends on the laser...

**Comment by ranranking** [comment]
Hi, there are some open questions to me. 

First of all, i will try to polish the readme and update all the information to the current stage.

Dichroic: We used 2 different dichroics, 740IY and FF660-DI02. If you want to use ~638 laser as excitation, the FF660-DI02 is a nice choice. The dichroic holder is aimed for standard beamsplitter set, 25x36mm dichroics and dia 25mm ex/em filter.

Beam size: Since the active area of the DMD2000 is 4.8x2.7mm, the laser beam was expanded to roughly 15mm and try to make the DMD area covered by the fast axis region.

**Comment by rwb27** [comment]
thanks @beniroquai and @ranranking that's helpful.  I've just been pricing up lasers - I will probably get some from Roithner, and I might get 50mW at 450nm (for GFP type stuff) and 100mW at 532nm.  Do you think that might be enough, or is the 300mW you reference really required?

**Comment by beniroquai** [comment]
I think this really depends on the QE of your fluorophore and the camera
used. We used some old SiR Rhodamine to label the Cells actin network.
Something was a bit odd with the buffer I assume since it was bleaching
like crazy - or the SiR was just old. GFP will be a lot dimmer I would
assume...but depends on the sample preparation of course. Synthetic dyes
always work better. You could try a GFP-booster with an AF647 dye?
 You will lose a lot of light at the DMD - especially if you want to have
multiple wavelengths and do not consider the blazed (532, 450 nm would need
to have a very fancy setup; or you have it separated of course)
@ranranking <https://github.com/ranranking> did something towards
multicolour SIM using DMDs. Not trivial at all.
Roithner is a good source. However, pricy. Laserlands.net is accepted by
our institute moreless. They have "good" quality lasers and deliver fast.

What'S the camera you want to use?

>

**Comment by rwb27** [comment]
Ah, when I said GFP type stuff I should have said fluorescein-type stuff, at least in the first instance I just want to image easy test samples to prove it works, so a nice bright dye is the right answer.  I am often guilty of interchanging fluorescein and GFP because they often use the same filters :$  I'm not proposing to make it nicely multicolour, just hedging my bets against which laser we'll eventually choose!  That said, if I've understood correctly you're basically imaging the DMD into the sample - so surely that should be OK across the visible spectrum?

**Comment by beniroquai** [comment]
Basically yes. Though you have the Fourier filter in the DMD-module. 
In terms of beam quality I'd go for the frequency doubled 532nm laser. They have nicer "single-mode" behaviour/gaussian profile.For the DMD module however, we would need to slightly correct the angle. If your student can operate Inventor that's no problem! If he cant, we can help! :-)
The incident angle need to match.

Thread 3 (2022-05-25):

### ISSUE TITLE
How to connect Raspberry Pi and DMD

### ISSUE THREAD

**Issue by rwb27** [openUC2/UC2_openSIM#3]
We've got the PCB to connect the Pi and the DMD board, and are currently waiting on the connectors.  However, the [photo](https://github.com/openUC2/UC2_openSIM/blob/main/IMAGES/DMDMontage.jpg) shows several jumper leads still used: we think the orange wire is connecting a pin next to the DMD power connector to the adjacent header, but what are the yellow wires doing?

**Comment by beniroquai** [comment]
Hey! Good point! If I remember correctly, the photo you see is the first version I designed that had some false connections. So I had a fun time to find them (based on [this blog post](http://frederickvandenbosch.be/?p=2948)). In the end I updated the eagle project with (hopefully) the correct connections. The version that I uploaded should be correct. We also have some boards here that we could send over (including connectors). We wanted to perform a SIM workshop in London actually - COVID came; did not happen ;-) ..

**Comment by rwb27** [comment]
Super - we'll hopefully confirm later this week whether the PCB from the repository works!

**Comment by beniroquai** [comment]
Great. Shame on me if it doesn't work.

**Comment by rwb27** [comment]
Thanks.  We’ve not yet tried to show an image, but we are struggling to get the DMD chip in the right place because the flex is so short.  Some of your pictures show an extension flex. Is that a custom piece or did you manage to buy it from somewhere?

**Comment by rwb27** [comment]
Also, is there an STL for the 45 degree holder for the raspberry pi somewhere?

**Comment by beniroquai** [comment]
Hey @rwb27 you are totally right. We tried to sneak in the DMD driver close to the display and indeed we had a second board, where we simply took the cable and extended the first one (worked surprisingly well). I'm not sure if these cables are for sale individually. I remember I checked it and found some somewhere. I think if you enter this strange number on the flatband cable in a naive google search you may find it. The 45° holder was some sort of an improvisation. It gets away the stress from the DMD back facet. @ranranking wasn't there another solution with just one cable too?

**Comment by beniroquai** [comment]
I found this image, but that's already fairly old and one of the very first prototypes:

![image](https://user-images.githubusercontent.com/4345528/140302738-ce212aa8-7032-40f7-b3fa-e57c47fb9519.png)

**Comment by ranranking** [comment]
Unfortunately i used two cables for the system, because the DMD chip and board will have a 90 degree angle and the cable they provided is really short. It might easily loosen contact from the DMD connector to the cable. Maybe get a longer cable is a better way to do it
![Cables](https://user-images.githubusercontent.com/52754557/140305161-bc6126df-364a-4004-a200-1c5f34e42f16.jpg)

**Comment by ranranking** [comment]
And you can find the STL file here https://github.com/openUC2/UC2_openSIM/blob/main/OLD/ASSEMBLY_CUBE_openSIM/30_CUBE_openSIM_DLP2000_Holder.stl

**Comment by jfr26** [comment]
Have you found these cables for sale separately?

Additionally, did you drill holes in the holder to screw in the DMD?

**Comment by ranranking** [comment]
The flex cable we didn't find a proper acess to buy them separately. That's why we connected two cables togther.

When you tear down the DMD from the EVM, it has two small screws which are used to mount the DMD board. We reused the screws and mount it onto the 3D printed part. On the part design, it already has 2 holes which are fit for mount the DMD board.

**Comment by beniroquai** [comment]
Don't worry too much about the missing cable. It will still work. We "just"
need to come up with a smarter way on mounting the Raspi + DMD Driver
board. Definitely doable.

Am Mo., 8. Nov. 2021 um 18:29 Uhr schrieb ranranking <
***@***.***>:

**Comment by rwb27** [comment]
@ranranking I didn't see any screw holes on the printed part, which seemed odd to me - I wonder if they might have been lost somehow?

We'll have a play with it in the lab tomorrow, hopefully we will figure out a mounting solution that's not too horrible!

**Comment by ranranking** [comment]
Hmm it is weird. When you check the preview of the stl file on GitHub, it shows the holes at least to me.
![image](https://user-images.githubusercontent.com/52754557/140925070-092f3af4-2d48-4afc-9935-ab7208c30360.png)
And it is like that when you mount the DMD board onto it.
![102c66c7efeb468d8c6df03ff18a087](https://user-images.githubusercontent.com/52754557/140925540-661ca774-30b3-423c-8050-c2671a19aa9c.jpg)
The holes are 1.5mm sized, maybe not printed there? Then you can drill a small hole for the screw. I think the screws are something like M2.

**Comment by rwb27** [comment]
The part I was looking at was the rectangular plate in the new integrated version of the SIM module (so the DMD is on a kinematic mount).  On closer inspection it did have the holes, they'd just closed up during printing.  I was able to open them up again with a 1.5mm drill.  The holes in the PCB are smaller than M2, but I found some very small self tapping screws that worked.

**Comment by rwb27** [comment]
For the record, our current solution is that we've got the DMD head mounted on the kinematic mount, and some custom holders based on the part pictured above supporting the DMD board.  The custom PCB is then plugged onto the DMD, and we've used a 40 pin GPIO extender between that and the Raspberry Pi, so the Pi sits flat on the bench.  This seems to work nicely, and the £3 GPIO extender was much easier to get hold of than the extender for the DMD ribbon cable.

The ribbon cable does foul the kinematic mount though - it works, but it's bent at a slightly alarming angle.  Did you have that problem too?

**Comment by beniroquai** [comment]
@ranranking I think the two photographs you are showing are originating from two different setups, or? The "kinematic" mirror attempt was the newer version if I'm not mistaking. Is this also part of the files in the github? 

@rwb27 the extension is a smart solution to get some space! Thanks! :) 
Also, I think we should summarize the parts that did not work out of the box in order to improve the documentation. Should we create a checklist somewhere? 

Thanks!

**Comment by ranranking** [comment]
@rwb27 Sorry, i was always confused about which version are you using. That's why i am sending randomly images of the two version. Its nice that you find the hole at the end. For the DMD cable, i must say it is very tricky. We used two DMD cables and were mounting the whole DMD board and Raspberry Pi to the cubes and SIM module in vertical direction. I am not sure if the part is in the Git, that time was thinking it's also not a idea solution.
![image](https://user-images.githubusercontent.com/52754557/143862385-769d9706-84a4-4a7f-910e-ba4ef626d1af.png)

**Comment by ranranking** [comment]
I uploaded the file to the Git as well, in case it is useful. The idea was pack the DMD board with the Raspberry Pi togther and mount them to the whole module. With two ribbon cables, it did not give a huge force to the cable nor the board.
https://github.com/openUC2/UC2_openSIM/blob/main/CAD/30_CUBE_openSIM_DMD_Raspi_holder.stl

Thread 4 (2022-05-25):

### ISSUE TITLE
Camera choice

### ISSUE THREAD

**Issue by rwb27** [openUC2/UC2_openSIM#4]
I realise that I have focused most of my efforts on the SIM module and not the rest of the microscope!  I think mostly it's just mirrors and UC2 cubes, but I realise there is a camera in there.  You specify "Allied Vision Alvium" but no model number.  What did you use? Which features were important?  I guess they are probably all fairly reasonable, but there's a big range of sensor sizes (and thus prices) so it would be good to know!  Did you use a USB version or MIPI with a Jetson Nano?

**Comment by beniroquai** [comment]
Hey, by the time we were starting the project we wanted to do everything on the Jetson Nano. Now after we gained lots of experience and talked to people we would rather go for another sensor I guess. We used the allied vision 158 Alvium chip (e.g. [Edmund](https://www.edmundoptics.de/p/allied-vision-alvium-1800-u-158m-129-158mp-c-mount-usb-31-monochrome-camera/44757/). It's cheap and works ok with the Jetson. Also I tried adapting the Openflexure to talk to this camera. We do STORM and SIM with it, but it does not talk to MicroManager.

We tried the MIPI and the USB version. MIPI uses the V4L2 interface that cannot provide the 12 bit stream for some reason. The USB version offers full VIMBA support which is actually very nice (Python, C bindings, etc.)

So the Huser Lab makes use of the Sony IMX174 in dSTORM and SIM. It has large pixels (5.6µm vs 3.4µm I guess) and higher QE. Costs a bit more, but I recently ordered a chip from Daheng that costs 500€. It has a python interface + jetson drivers too (see SQUID paper from the Prakash Lab; [European distributor](https://www.get-cameras.com/USB-Camera-3.0-2.3MP-Monochrome-Sony-IMX174-MER2-230-168U3M). 
IDS and Basler has the sensor, costs a bit more, but has much better drivers it says. 

The IDS and Daheng IMX 174 should arrive in the next weeks. I can tell you more then! :) 

Alternatively: SIM with the Raspberry PI would be fun. Synthetic dyes + high laser power could totally make that happen. Sampling is then of course a fun thing ;-)

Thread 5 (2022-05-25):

### ISSUE TITLE
I2C bus on the Pi

### ISSUE THREAD

**Issue by jfr26** [openUC2/UC2_openSIM#5]
The I2C bus on the Pi 4 is different from that on the Pi 3. Does this affect the interaction with the DMD board? Following the setup instructions as given on this Github does not work with a Pi 4 at the moment.

https://docs.microsoft.com/en-us/windows/iot-core/learn-about-hardware/pinmappings/pinmappingsrpi

https://www.etechnophiles.com/raspberry-pi-4-gpio-pinout-specifications-and-schematic/#:~:text=Raspberry%20Pi%204%20GPIO%20Pinout%20has%2040%20pins%3A,supports%20SPI%2C%20I2C%2C%20and%20UART%20serial%20communication%20protocols.

**Comment by jfr26** [comment]
I managed to get an image by using

i2cset -y "ffffffff00000002.i2c" 0x1b 0x0b 0x00 0x00 0x00 0x00 i
i2cset -y "ffffffff00000002.i2c" 0x1b 0x0c 0x00 0x00 0x00 0x1b i

instead.

**Comment by beniroquai** [comment]
Hey @jfr26, I already heard from your problems you were facing from @rwb27. "you see an image" means, it works?! :) 
Would you mind making a PR to add this to the docu? also if you have any notes, where you got stuck in the documentation, please blame me for improving it! I think it is not fully reviewed so that others can replicate it easily. 
Thanks! :)

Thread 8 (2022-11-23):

### ISSUE TITLE
Parts out of production; replacement suggestions

### ISSUE THREAD

**Issue by b2jia** [openUC2/UC2_openSIM#8]
Thanks again for providing this amazing public resource!

A couple of questions:

- Tube-lens : the f=180 mm lens from PGI-Versand no longer appears to be available. Is there a part from ThorLabs the authors might be able to recommend? Is there enough tolerance to accomodate an f = 200 mm lens such as [AC254-200-A-ML](https://www.thorlabs.de/thorproduct.cfm?partnumber=AC254-200-A-ML)
- Dichroics : it seems the ComarOptics 740 IY 125 40x25mm is also no longer available. Is the [DMLP638R] (https://www.thorlabs.de/thorproduct.cfm?partnumber=DMLP638R) a suitable replacement? Dimensions are a bit off (36x25mm) and the cut-on wavelength is close but not exact.

**Comment by ranranking** [comment]
Hey,
thanks for reaching us!

- for the tube lens, sure zou can exchange it with thorlabs 200mm lens. As the imaging part is separate sitting on the ground floor, it should be fine to adjust it into infinity. Just be aware that the cube has 50mm size, so it could be the right position of the lens sits somewhere between two cubes. If it is like that, you might need to have a short extend thorlabs 1inch tube to satisify it.
- the 638R seems fine to me, the only problem to me is cuton wavelength is quite near to the emitting laser. It might need a bit higher output so you can get enough on your sample. Otherweise this dichroic might fits the wavelength better, but also a bit expensive. https://www.thorlabs.de/thorproduct.cfm?partnumber=DMLP650R  But both should be working.

If you get any new problem, just write us back, i will try to help you out.
Best Regards

**Comment by b2jia** [comment]
Thanks for your response! 

- Just to confirm, by extension tube, it is just a simple [stackable lens tube ie. (SM1L10)] (https://www.thorlabs.com/thorproduct.cfm?partnumber=CM1L10), this looks sufficient?
- In case others are also reading this thread, Chroma has some reasonably priced dichroics: https://www.chroma.com/products/parts/t647lpxr

**Comment by ranranking** [comment]
I was expecting some tubes like that https://www.thorlabs.com/thorproduct.cfm?partnumber=SM1L03
if you want to use c mount ones, i think you need to screw it onto your camera. I dont think you can screw it into thorlabs cages

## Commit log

2021-07-14 Code for synchronise between raspberrypi + camera
    00_ create the grating pattern with pygame on the DMD, Vimba controll the allied version camera and wait for external trigger to capture image sequences
2021-08-16 The 3D printed parts for openSIM
2021-11-29 Add files via upload
    Raspberry Pi mount
    [30_CUBE_openSIM_DMD_Raspi_holder.stl]
2022-05-25 add the microscrew driven z-stage
    [20_Cube_Insert_Z-Focus_single_v3.stl]
